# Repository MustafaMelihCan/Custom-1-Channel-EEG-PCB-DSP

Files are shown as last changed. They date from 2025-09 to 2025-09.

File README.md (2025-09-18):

# Custom-1-Channel-EEG (PCB + DSP)

A custom single-channel EEG device developed from PCB design to real-time brainwave visualization.  
Features a low-noise analog front-end with filtering, STM32 DSP (biquads, Welch’s method), and verified alpha detection (~6 dB SNR, ~5× alpha power). See the report to understand how the system works: [Custom 1-Channel EEG Report](docs/Custom_1-Channel_EEG_Device_From_PCB_to_Brainwaves.pdf).

---

## Demo
▶️ Watch the demo video here: [YouTube Link](https://youtu.be/_DtyJymNVPs)  

**Report (PDF):** [Custom 1-Channel EEG Report](docs/Custom_1-Channel_EEG_Device_From_PCB_to_Brainwaves.pdf)

---

## Repository Layout
- `hardware/` – Gerber files, drill files, BOM, LTspice simulations
- `firmware/` – STM32 (CMSIS-DSP) source code and project files
- `docs/` – report, schematics, images

---

## Quick Start
0. To get an overview of the system look at `/docs/1 Channel EEG System Pipeline Final version`. 
1. Build firmware with STM32CubeIDE (or compatible toolchain).  
2. Order PCB using Gerber files from `/hardware/`.  
3. Source components using the BOM in `/hardware/`.  
4. Connect electrodes: **O2** (active), **mastoid** (reference), **Fz/forehead** (DRL).  
5. Stream band powers over USART and visualize with a serial plotter.

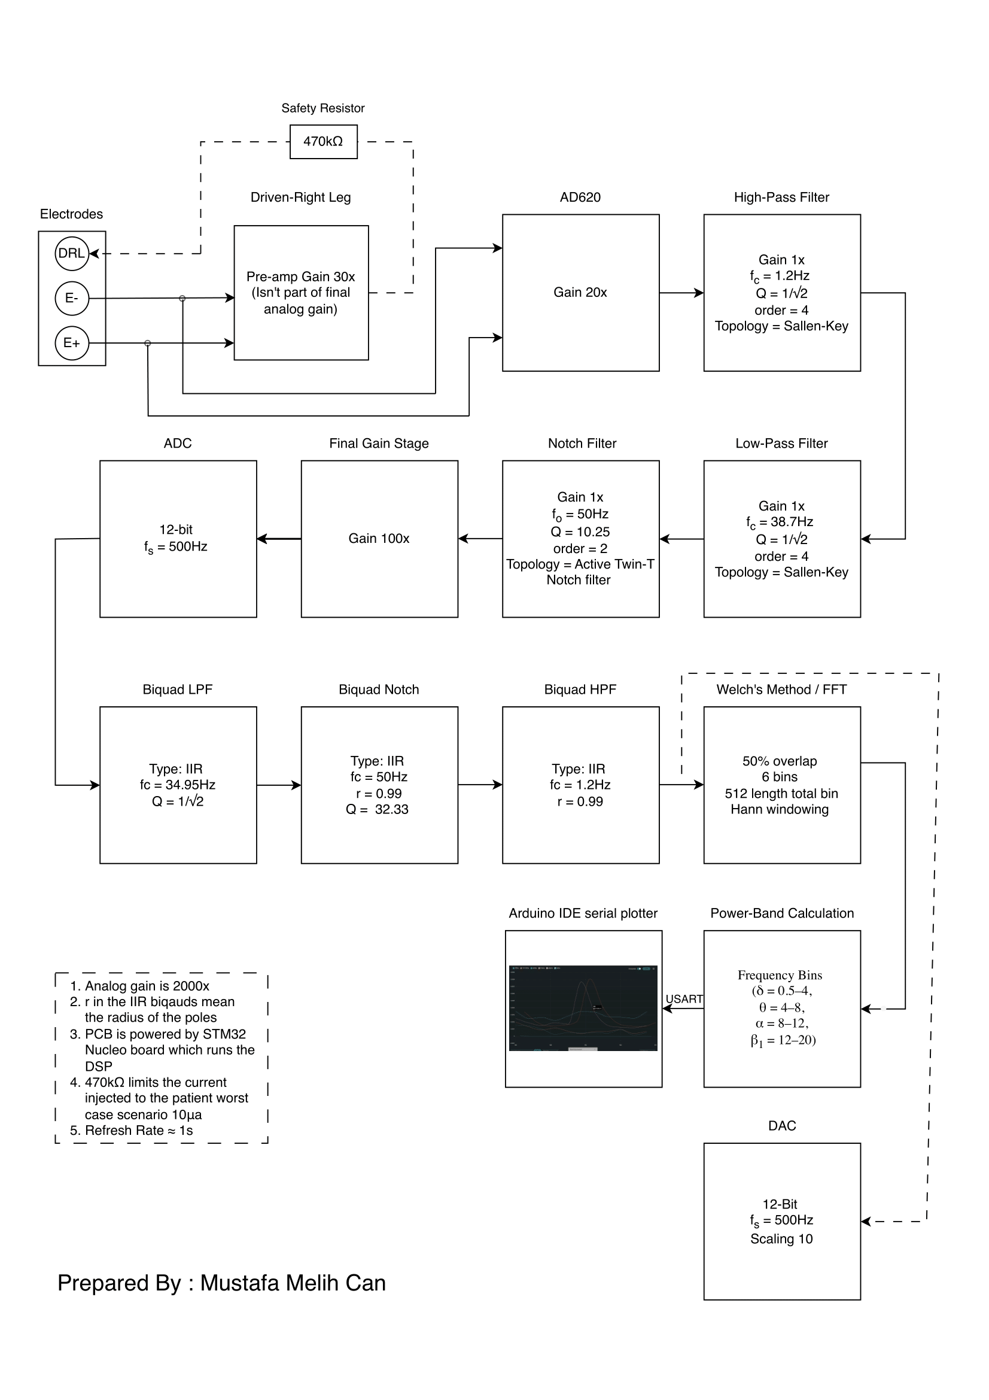
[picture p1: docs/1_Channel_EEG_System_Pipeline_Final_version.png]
EEG System Pipeline


---
## Firmware (STM32 NUCLEO Boards)

The firmware is provided as a zipped STM32CubeIDE project in `/firmware/EEG_Firmware.zip`.  
This code runs on STM32 NUCLEO boards (tested on NUCLEO-F446RE, but portable to other STM32 MCUs).  

### How to use:
1. Download and unzip `EEG_Firmware.zip`.  
2. Open **STM32CubeIDE**.  
3. Go to **File → Import → Existing Projects into Workspace**.  
4. Browse to the unzipped folder and select the project.  
5. Build the project (CubeIDE will compile the code automatically).  
6. Connect your NUCLEO board via USB.  
7. Click the **Run/Debug** button in CubeIDE to flash the firmware.

### Pinout (NUCLEO-F446RE)
- **PC3 (ADC3_IN13)** → EEG analog input from PCB  
- **PA4 (DAC_OUT1)** → Filtered signal output (scope/debug)  
- **PA2 (USART2_TX)** → Serial output to PC (band powers)  
- **PA3 (USART2_RX)** → Not used  
- **PA5 (LD2 LED)** → Status indicator (DMA callbacks)  
- **5V & GND rails** → Power for analog PCB  

Once flashed, the board will:  
- Sample EEG signals from the analog front-end.  The ADC is the PC3 pin. 
- Apply DSP (biquads, Welch’s method) in real time you can see the output on PA4. 
- Stream band power values (Delta, Theta, Alpha, Beta) via USART for visualization.
- You can power the PCB using the 5V and GND rails on the Nucleo Board

**Note:** You can view the streamed data using Arduino IDE’s Serial Plotter or any terminal that supports plotting.  

---
## License
- **Code**: MIT License  
- **Hardware**: CERN OHL-W License (see `/LICENCE_Hardware`)
## Disclaimer
- This project is intended for educational purposes only.  
- The creators accept no responsibility for any harm or misuse resulting from its application.

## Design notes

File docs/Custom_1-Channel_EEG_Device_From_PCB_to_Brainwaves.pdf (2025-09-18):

Mustafa Melih Can | Custom 1-Channel EEG Device: From PCB to Brainwaves

# Mustafa Melih Can Custom 1-Channel EEG Device: From PCB to Brainwaves

# Abstract

This project presents the design and implementation of a custom single-channel electroencephalography (EEG) device developed from printed circuit board (PCB) fabrication to real-time brainwave visualization. The system integrates an analog front-end for amplification, filtering, and common-mode noise rejection with digital signal processing on an STM32 microcontroller. Core algorithms include biquad filters and Welch’s method for spectral estimation, enabling reliable suppression of 50 Hz interference and white noise. The device was validated through the detection of alpha activity during eye closure, achieving a signal-to-noise ratio of approximately 6 dB and an alpha power increase of 5.2 times compared to the eyes-open condition. Despite limitations of its single-channel architecture and sensitivity to electrode placement, the results demonstrate that a low-cost DIY EEG can capture meaningful neural activity. The project provides a foundation for future improvements such as multi-channel expansion, wireless communication, and advanced artifact rejection techniques. It allows for a Digital Signal Processing (DSP) based EEG device that can be used in research / commercial / DIY use.

# Introduction

Electroencephalography (EEG) is a non-invasive method of measuring brain activity by detecting voltage fluctuations generated by neural oscillations. It plays a crucial role in clinical diagnostics, neuroscience research, brain–computer interface (BCI) applications, and consumer neurofeedback devices. However, most commercial EEG systems are costly, complex, and designed for multi-channel use, making them less accessible for students, researchers, and hobbyists who seek to explore neural signals at a smaller scale. At the same time, do-it-yourself (DIY) EEG projects often struggle with fundamental challenges such as low signal amplitude, environmental noise, and electrode stability. To address these limitations, this project set out to design and implement a custom single-channel EEG device that is affordable yet capable of reliably detecting meaningful brainwave activity. The system integrates an analog front-end with amplification and filtering, digital signal processing on a microcontroller, and real-time visualization of EEG band powers. By focusing on detecting alpha activity during eye closure as a proof of concept, the project demonstrates how a streamlined design can bridge the gap between academic prototyping and practical EEG experimentation. The project aims to create a reliable system to detect brain signals.

# System Overview

The EEG consists of three main parts in this project. The system is divided into three stages: Analog, Digital, Display. Because the main purpose of this study is to make a single Channel device and mixed signal analysis Analog and Digital parts of the project got more attention. The Analog side design flow progressed as LTspice simulation, Breadboard Filter Prototyping and testing, to PCB design, soldering and testing. You can see the full project pipeline on Figure 1.

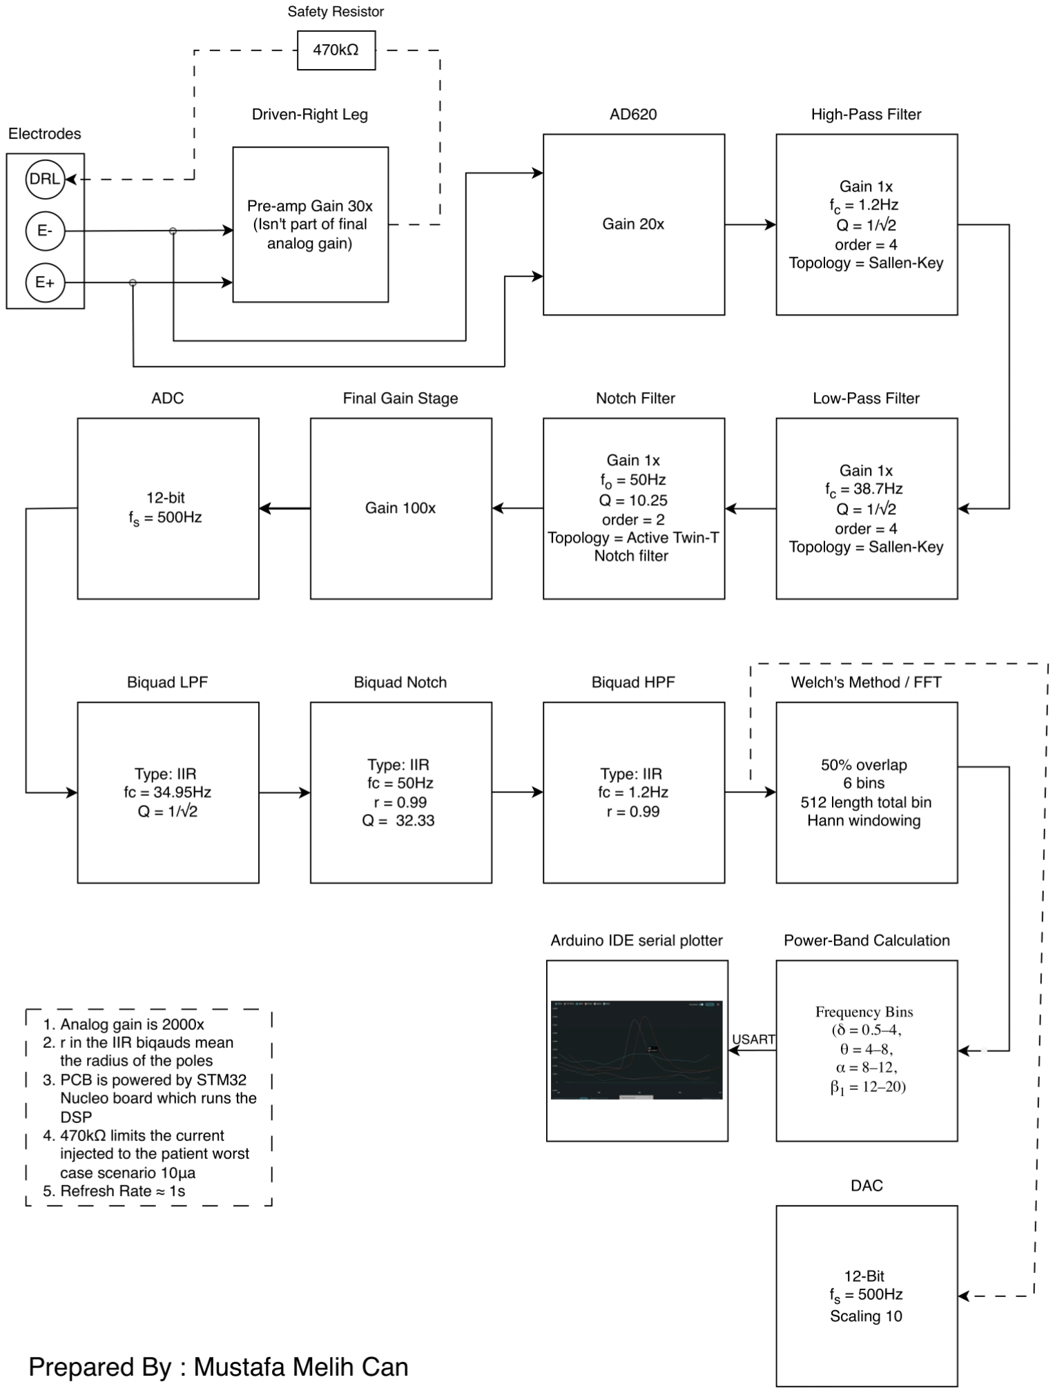
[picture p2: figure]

Figure 1. 1 Channel EEG System Pipeline

The analog stages “prepares the signal” by adding a total gain of 2000x and does filtering for a clearer and aliasing-free signal. According to Nyquist theorem fs > 2fmax; I chose fs = 500Hz (~10× fmax) to make the signals smoother on the DAC.

# Hardware Design

Ok the hardware has two important roles. The first is Common Mode Noise Rejection (CMNR) that is accomplished through Driven Right Leg (DRL) and Instrumentation amplifier (INST AMP) stages. The second role is filtration and adding gain.

## Common Mode Noise Rejection

The DRL is the first line of defence in us improving Signal to Noise Ratio (SNR). It basically averages the E+ and E-, adds gain, inverts it and sends it back to the body with a current limiting resistor. We basically use an adder topology since 30 ⁽x1+x2

)
2

= 15(x1 + x2

).

Here is the DRL block and the INST AMP schematic on figure 2:

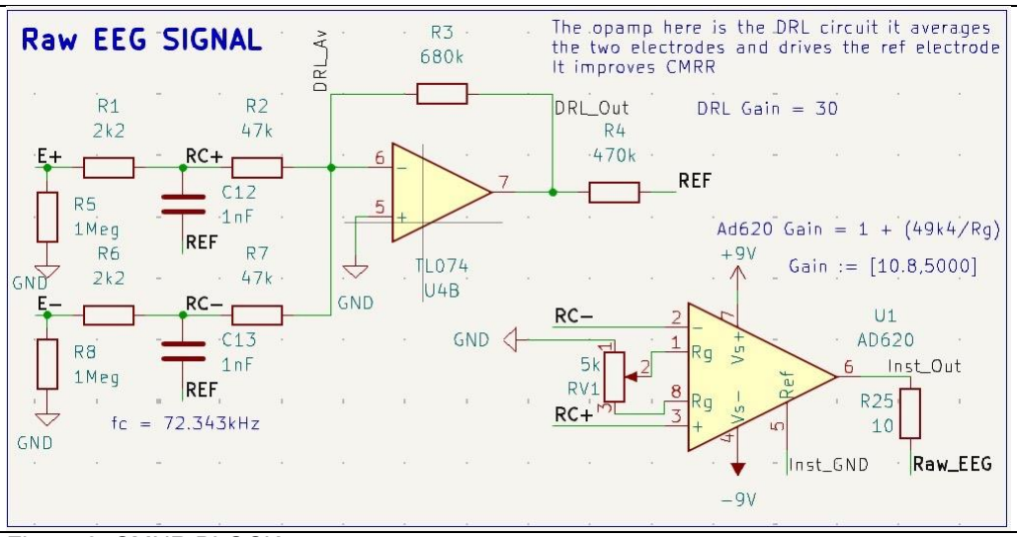
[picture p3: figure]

Figure 2. CMNR BLOCK

As you can see the basic DRL has some additions in design. I added a 1MΩ to the GND to make sure that the electrodes wouldn’t float if they are not connected to anything else. Then the electrode stages depicted by E- and E+ connects to an RC lowpass stage with a fc at 72.34 kHz this is done to clean the signal before the signal reaches the INST AMP. And since the fc is far away we don’t need to make it active and can get away with a passive one. Then we have the DRL stage with the H(s) as follows:

30 ⋅

Vin1

(s) + Vin2

(s)
2

= Vout(s)

Plus the DRL has a current limiting which limits the max current to: Vmax
R4 =

5V
470kΩ

= 10μA

After the DRL stages we feed the RC+ and RC- stages to our INST AMP with a gain setting equation as follows:

Gain = 1 +

49k4
RV1

: {RV1 ≔ [1,5k]}

RV1 is a potentiometer (POT) so we can write the gain range of the INST AMP as follows: Gain : {[10.8,5000]}
However, the gain i used is 20x for the inst amplifier and for your project it should get max of 100 to 200 to not swamp the EEG signal with further 50Hz hum and white noise we can add the further gain needed later. Why did we choose the gain 20x for now because alpha jumps and general eeg signals are around 10 to 20uV we if we want to make them as large as possible however we generally have a 50Hz hum that can be as large as 100mV to 250mV.

Considering these the max gain is calculated to maximise eeg signal while not saturating our opamp range ±5V ; when we pick the gain around 20x that is the ideal spot hum and eeg signal volts are as follows:
VEEG ⋅ G = 20μV ⋅ 20 = 0.1mV V50Hz ⋅ G = 250mV ⋅ 20 = 5V As you can see the main constraint for our initial INST AMP gain stage is the environmental hum. The gain setting is set using a POT as you can see from the Figure 2. Pot works as a INT AMP gain setting.

## Filtering and Gain Stage

### a. High-Pass Filter (HPF)

The purpose is to remove motion, breathing, DC offset and heartbeat artifacts below 1.2Hz. 4th degree filter is decided to be made because the phase distortion by the 4th order is considered acceptable, therefore the order is not a constraint. And breathing artefacts and heartbeat artefacts wanted to be removed as efficiently as possible. So by cascading two second order HPF’s i decided to get a 4th order HPF the second order HPF transfer function is as follows:

HHP(s) =

s

2

s

2 +

ωc
Q

s + ωc

2

The Sallen-Key 2nd order HPF topology is used. Please see the appendix to see the derivation of the transfer function which results in our topology seen in figure 3. and the transfer function seen is as follows:

HHP(s) =

s

2

s

2 +

c1 + c2
c1 ⋅ c2 ⋅ R2

s +

1
c1 ⋅ c2 ⋅ R1 ⋅ R2
Please check appendix for the derivation.

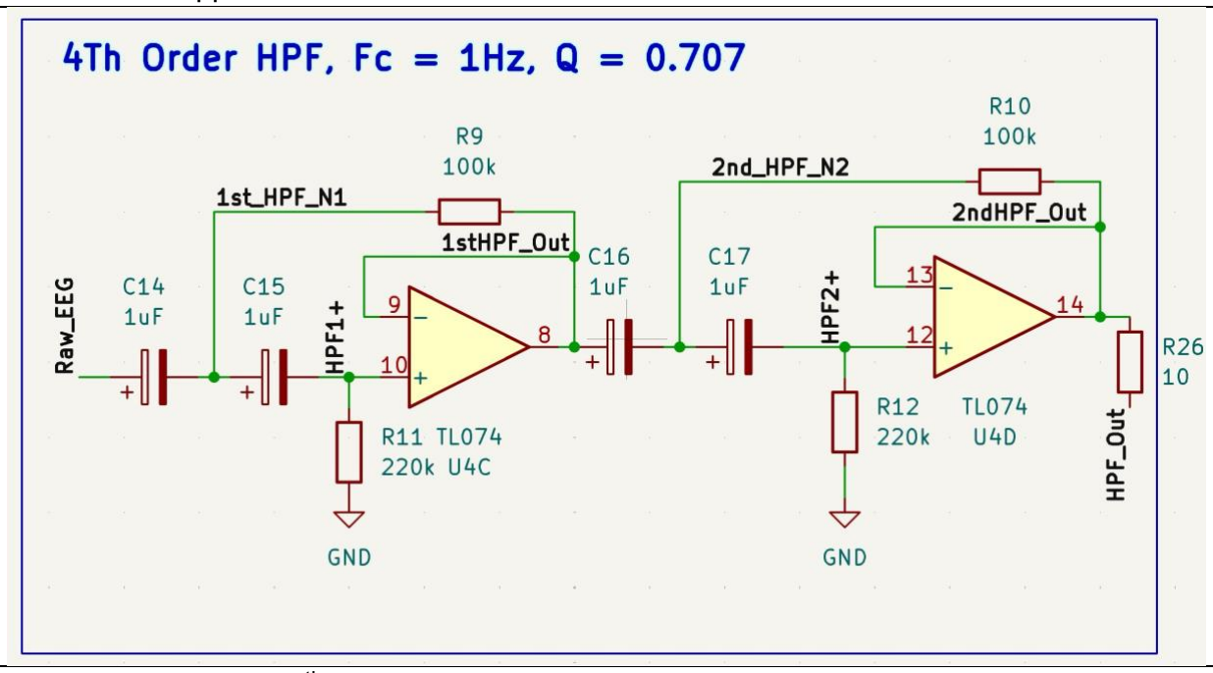
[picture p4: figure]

Figure 3. Sallen-Key 4

th order HPF

Using the transfer previous transfer functions we get the equalities:

ωs
Q

=

c1 + c2
c1 ⋅ c2 ⋅ R2

ωs

2 =

1
c1 ⋅ c2 ⋅ R1 ⋅ R2
Our desired fc = 1Hz and Q =

1
√2

which creates a Butterworth filter. fc is chosen as higher than

usual eeg devices to remove the breathing and heartrate artefacts more efficiently since we cannot use ICA algorithm like multiple channel electrodes we need to remember that we have a single channel eeg so cleaner is always better and our purpose is to catch alpha and low beta waves so we can compromise some data lose in the delta wave range. We can choose the capacitor values arbitrarily and values that are physically easy to find and implement we can choose both capacitors as 1μF which when we seperate R1 and R2 we get the following equations (R1=R11=R12, R2=R9=R10, C1=C2=C14=C15=C16=C17):

R2 =

Q ⋅ (c1 + c2

)
c1 ⋅ c2 ⋅ 2 ⋅ π ⋅ fc

= 225kΩ ≈ 220kΩ

R1 =

1
c1 ⋅ c2 ⋅ (2 ⋅ π ⋅ fc

)

2 ⋅ R2

= 112kΩ ≈ 100kΩ

To verify we plug our R1, R2, C1, and C2 back to our equations to find fs and Q. Which when we plug them in we get them as:
Q = 0.741, fc = 1.08Hz

### b. Low-Pass Filter (LPF)

The purpose is to remove EMG and power line noise and also to act as our antialising filter HPF for further DSP application. A similar decision made to HPF made in our LPF as well a 4th order filter with –24dB/octave is chosen. Because both EMG which is between 30Hz to 100Hz range and 50Hz hum is are strong noise sources which we want to eliminate as strongly as possible. The topology is at Figure 4.

Figure 4. Sallen-Key 4th order LPF
A similar design process to HPF is followed therefore the details are omitted. However the final Q and fs are as follows:
Q = 0.755, fs = 38.79Hz

### c. Notch Filter

The purpose is to remove power line noise in Turkey with standard 50Hz. An active Twin-T notch filter is used for our design. Because we can set the Q using a simple voltage divider and the Twin-T topology doesn’t determine the Q and we can use them to control the center frequency also with this topology we only use 2 opamps. The topology can be seen in Figure 5.

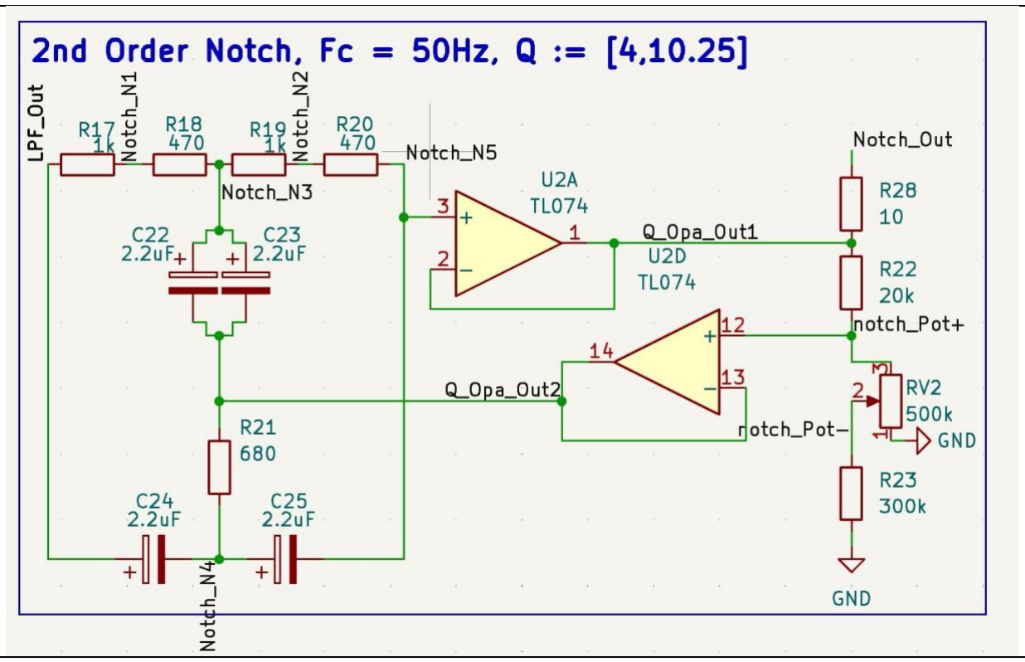
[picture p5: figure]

Figure 5. Active Twin-T Notch Filter
For context of my circuit lets the set values are as follows: R17 + R18 = R19 + R20 = R, R21 =
R
2

, C22 = C23 = C24 = C25 = C
The following contains the transfer function of the Notch Filter:

HN(s) =

s

2 + ω0

2

s

2 + s

ω0
Q

+ ω0

2

=

s

2 + (

1
RC)

2

s

2 + s

4 ⋅ (1 − K)
RC + (

1
RC)

Where:

K =

RV2 + R23
R22 + RV2 + R23

Q =

1
4(1 − K)

so, Qmin = 4, QMax = 10.25

Since RV2 is a potentiometer, it was used to tune the effective gain range [4,10.25], so that it can attenuate 50Hz while not cause ringing in the circuit that is why it is capped at 10.25 value.
f0 =

1
2πRC

= 50Hz

f0 =

1
2πRC =

1
2π ⋅ 1.470 ⋅ 10³ ⋅ 2.2 ⋅ 10⁻⁶ = 49.21Hz ≈ 50Hz

Be careful when increasing the Q on your project with the potentiometer because as you can see the center frequency in our case is around 49.21Hz and if we increase the Q very high such as 30 40 we might make the notch very steep and deep causing our filter to miss the center frequency which is 50Hz in our case.

When we simulate all of the filters in LTspice we get the following filter response:

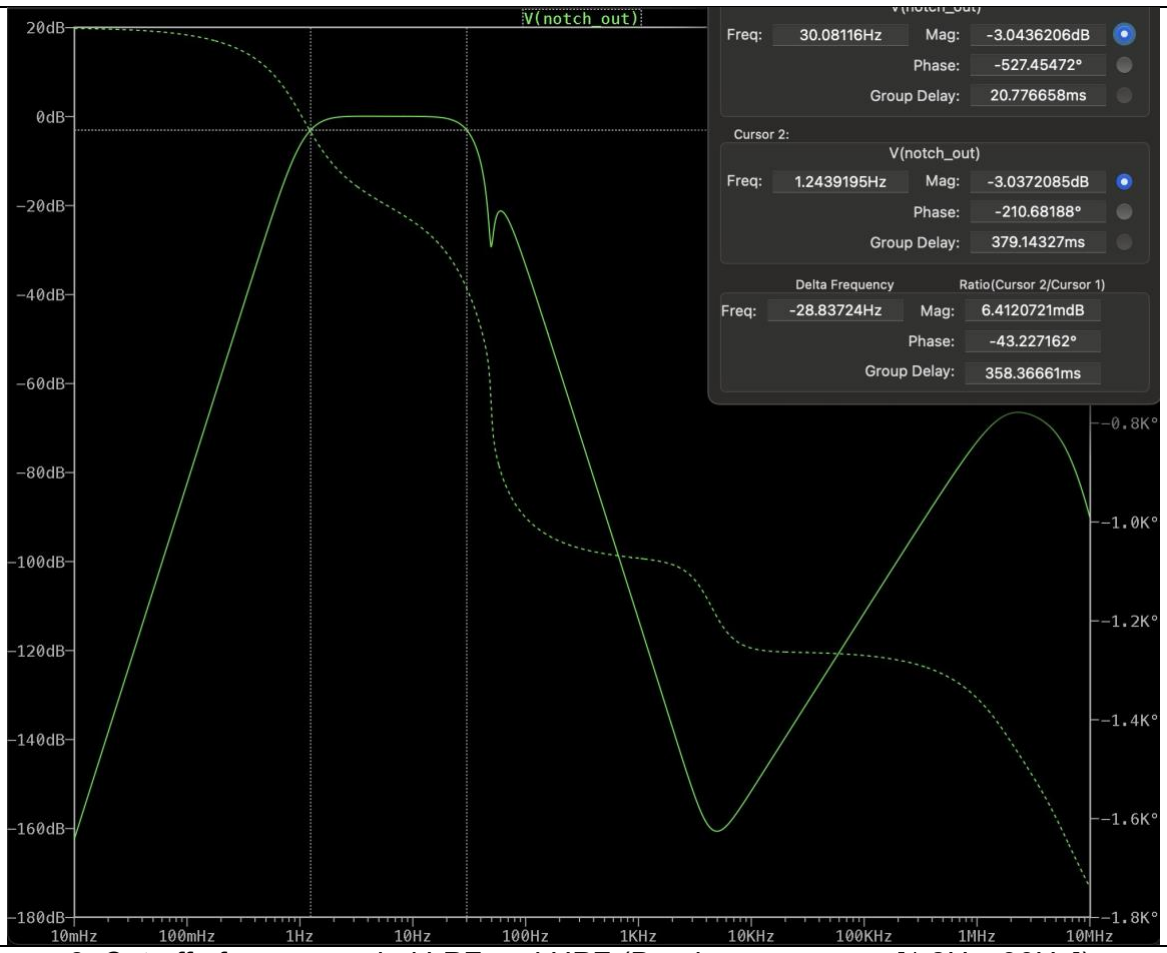
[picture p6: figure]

Figure 6. Cut off of our cascaded LPF and HPF (Bandpass range := [1.2Hz, 30Hz])

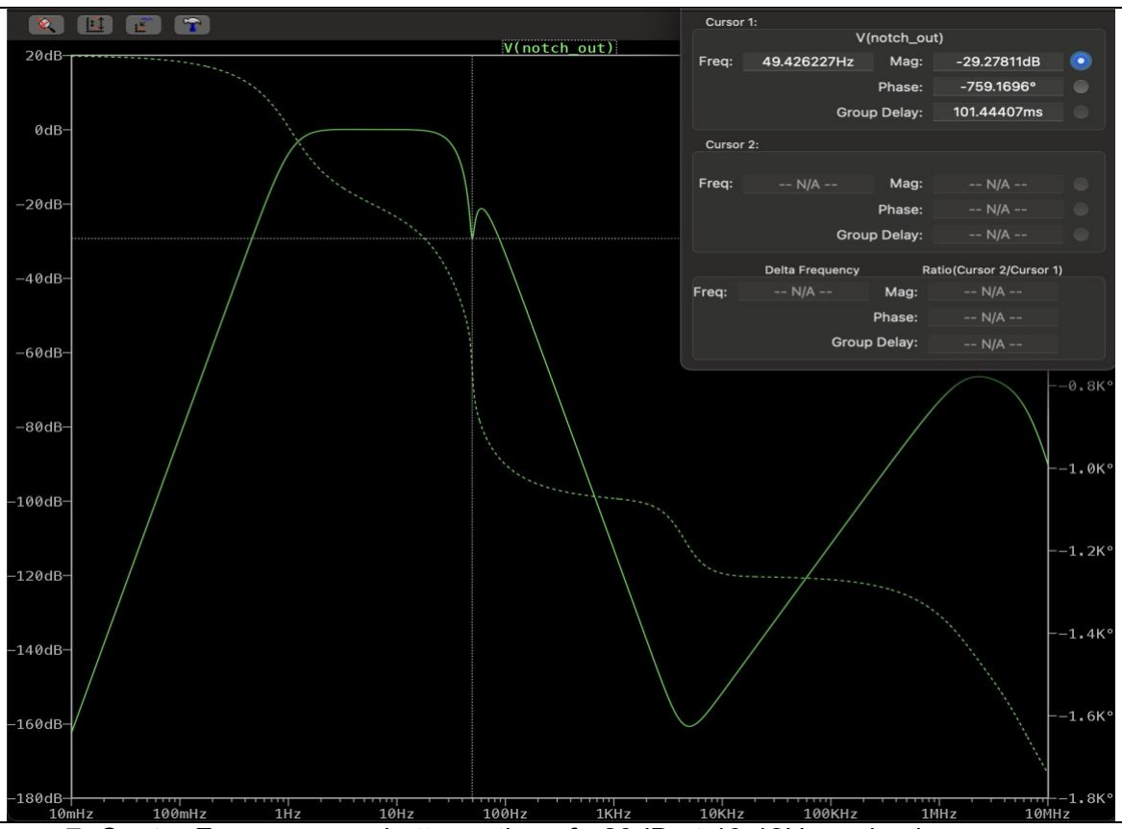
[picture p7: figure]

Figure 7. Center Frequency and attenuation of –29dB at 49.42Hz mains hum

### ç. Final Gain Stage

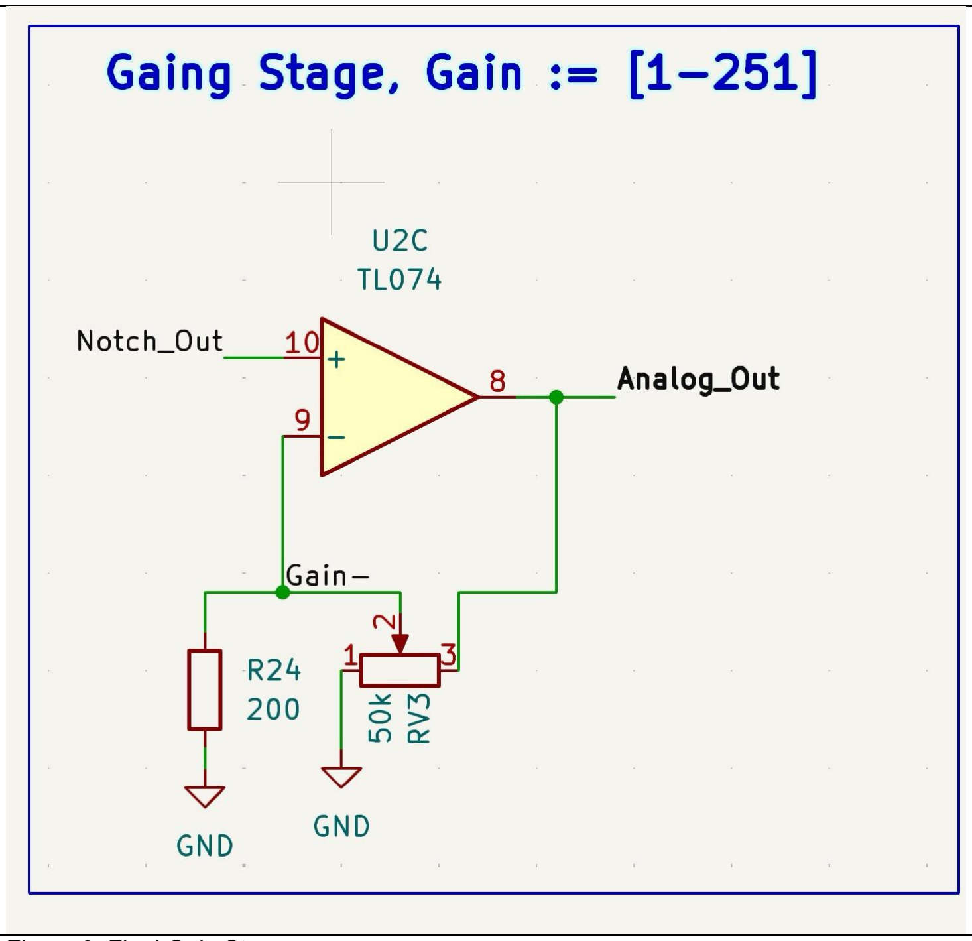
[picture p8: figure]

Figure 8. Final Gain Stage The Gain function is as follows:

Gain = 1 +

Rv3
R2

, Rv3 ∈ [0,50kΩ], R2 = 200Ω

This final stage gives a gain setting with a potentiometer between 1x to 250x. Allowing me to set the output of the PCB between the ADC optimum range which is between 0V and 3.3V. This gain stage allows for a DC offset adder as well because the PCB output is generally is around 200mV so we can easily increase the gain to add a 1.65V DC offset that will make the output of the PCB optimum for the ADC stage. If yours doesn’t come out like that you can add a DCshifter which you can find the design on the appendix section.

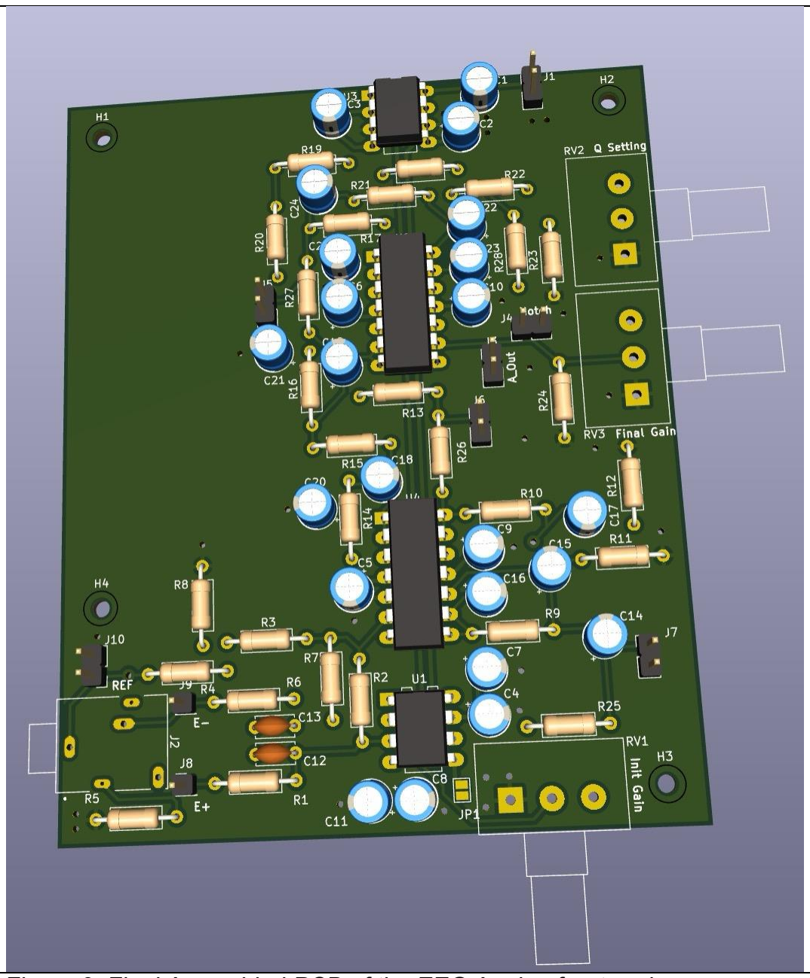
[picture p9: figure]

Figure 9. Final Assembled PCB of the EEG Analog front-end

# Software Design

The software in this project completes the rest of the functionalities of the EEG. There are two functions that the digital side accomplish:
1) Digital Signal Processing
a. Welch’s method (Reducing white noise)
b. ARMA Biquad Filters (Remove hum, artefacts)
2) Displaying EEG Frequency Bands
a. Do Fast Fourier Transform (FFT) and calculate Power Spectral Densiy (PSD) to show different frequency ranges (Alpha, Beta, etc.)
b. Data Display: Using USART to show data on a serial display
An appropriate Sampling frequency 500Hz is chosen. It is 15x the max frequency (35Hz) that our system will be interested. And is well over the nyquist theorems minimum sampling frequency (fs>2fmax).

## Digital Signal Processing

### A. Biquad Filters

A biquad filter basically means a two zero, two pole cascading second order (SOS) filters. The SOSs can be cascaded without making the whole system unstable they act as the building blocks of our larger complicated filtering systems. In this instance we want to create the same filters we created in the analog side to further clean our signal digitally. A biquad equation has the form:

H(z) =

b0 + b1z

−1 + b2z

−2
a0 + a1z

−1 + a2z

−2
The form then can be turned into the difference equation using inverse Z transform:

y[n] = b0x[n] + b1x[n − 1] + b2x[n − 2] − a1y[n − 1] − a2y[n − 2].

The difference equaion results in the following figure configuration:

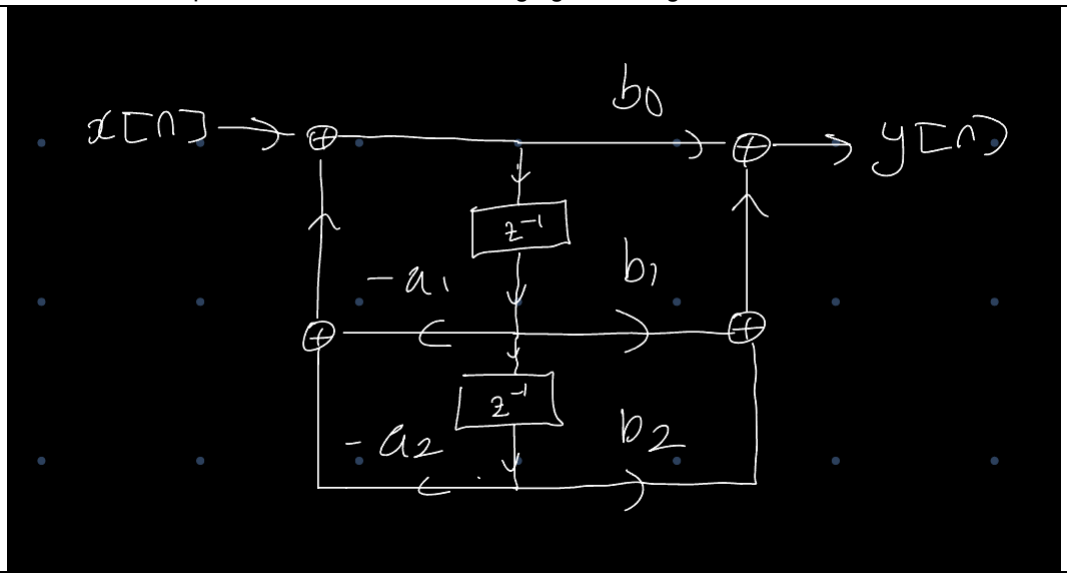
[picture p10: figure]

Figure 10. Cascade form of ARMA Biquad Filter Block Diagram

By using CMSIS-DSP library of the ARM cortex MCU’s when we get the coefficents of our filters we basically can plug them in the CMSIS functions. Which will do the multiplying and shifting of our buffer for us which depicted on the Figure 10.

### A1. Biquad Notch Filter

To get a notch filter we are going to put zeros at 50Hz and poles around 50Hz with the radius r1. Using our sampling frequency, to calculate that region we use the formula:
ω = ΩT;
Where Ω means the analog angular frequency, ω is the digital angular frequency and, T is our sampling period.

Assuming we want to place our zeros and poles at 50Hz then to find where are we going to place them between [-π, π] which is digital angular frequency range:

ω0 = Ω0T = 2π ⋅

f0
fs

= 2π ⋅

50
500 =

π
5
Here we see that our poles/zeros should be on the π/5. However, since our filter needs real coefficients we are going to put them at ω0 =

π
5

, −

π
5

on the complex plane. Plus we going to place the zeros right on the unit circle making a very deep notch and placing the pole near the zero but not at unit circle. This is done to dampen the notch effect and control the notch by controlling the radius of our poles. Lets see the mathatical formulation:

HN(z) =

(1 − z
−1e

j

π
5) (1 − z
−1e

−j

π
5)

(1 − z
−1r1e

j

π
5) (1 − z
−1r1e

−j

π
5)

HN(z) =

1 − 2 cos (

π
5

) z
−1 + z

−2

1 − 2r1 cos (

π
5

) z
−1 + r1

2
z

−2

Therefore our notch equation is completed.

Figure 11. Notch Filter Response |H(e^jw)|

When we try some r1 values and simulate the results on Matlab we get an r1 value of 0.99. Which we can see the results on Figure 11. and the pole-zero plot on figure 12.

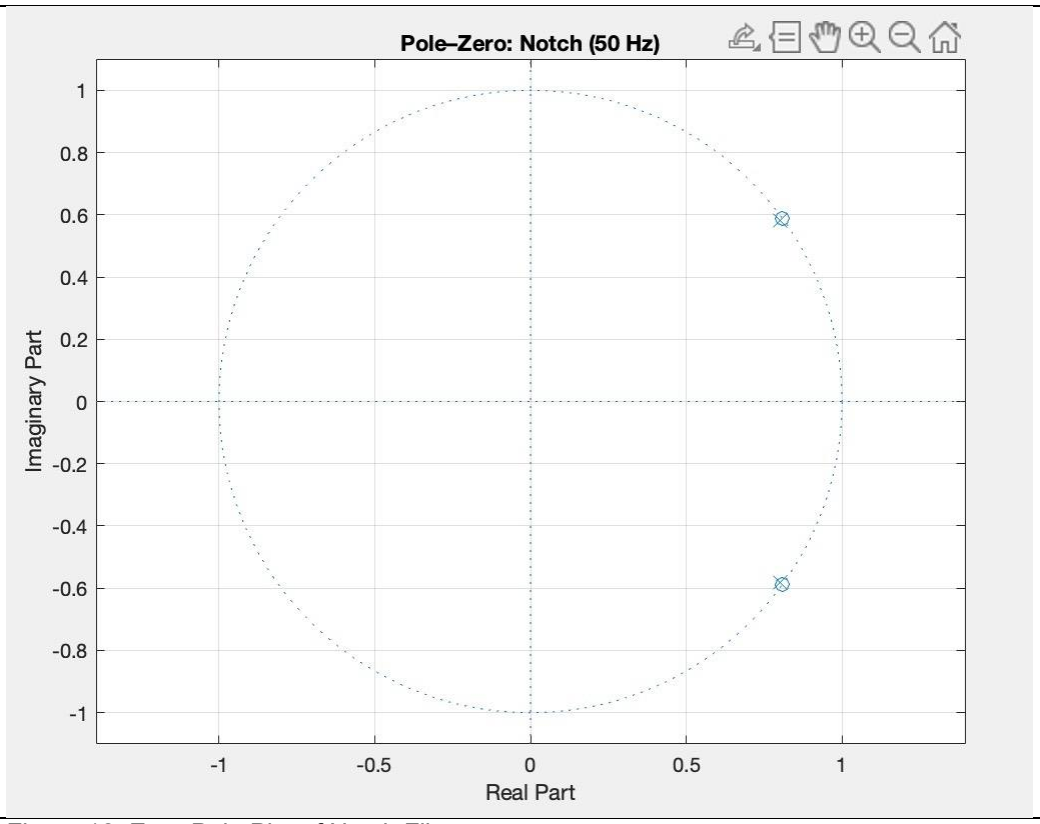
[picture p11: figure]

Figure 12. Zero-Pole Plot of Notch Filter

The final coefficients are:
bnotcℎ = [1, − 2 ⋅ r1 cos (

π
5

) , 1]

anotcℎ = [1, −2r1 cos (

π
5

) , r1
2

]

### A2. Biquad HPF

Standard HPF and LPF biquad designs are used. The HPF is designed as:

HHP(z) =

(1 − z

−1
)

2
(1 − r2z

−1)

2

HHP(z) =

1 − 2z

−1 + z

−2
1 − 2r2z

−1 + r2

2
z

−2
And:
r2 = exp (−

2πfHP
fs

) = exp (−

2π1.2
500 ) = 0.985

Here is the Pole-Zero plot of the filter:

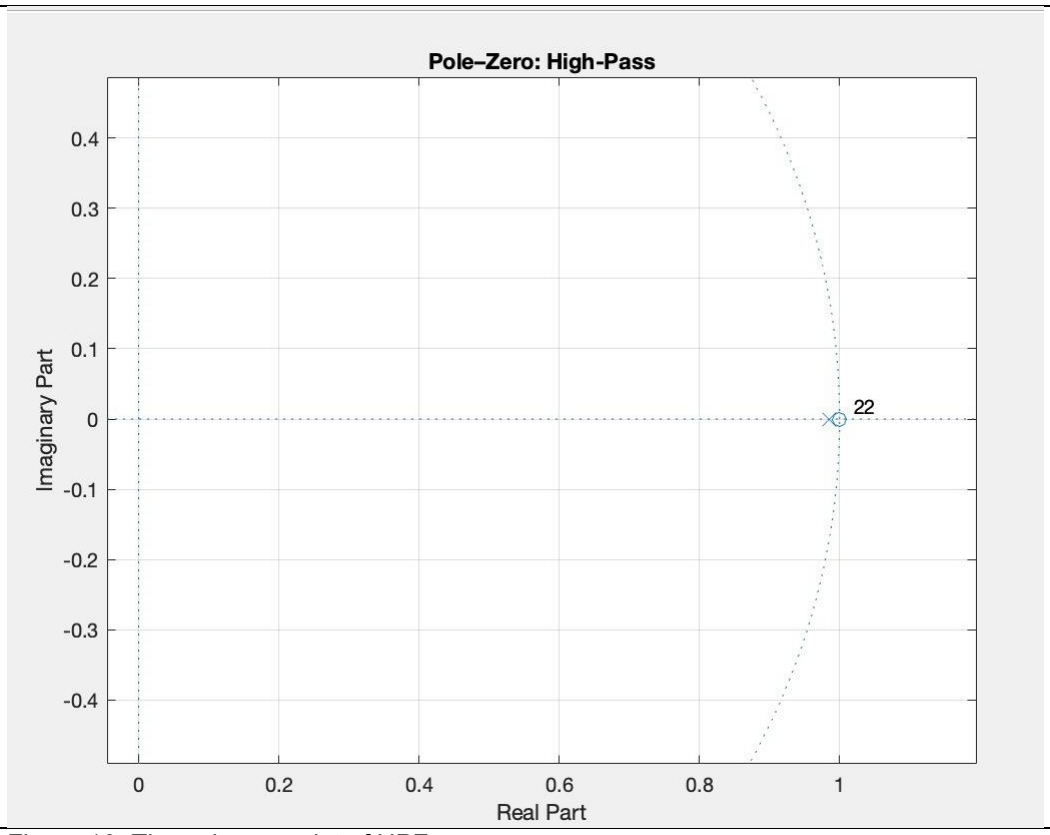
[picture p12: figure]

Figure 13. The pole-zero plot of HPF
As you can see from the figure 13. our biquad pole and zeros are on the real axis which is consistent with our desgin choices and our application. Now we must find the HPF coefficients therefore the coefficients for the HPF is found:
bHPF = [1, − 2, 1];
aHPF = [1, − 1.980, 0.9801]; With these coefficients we get the following filter response:

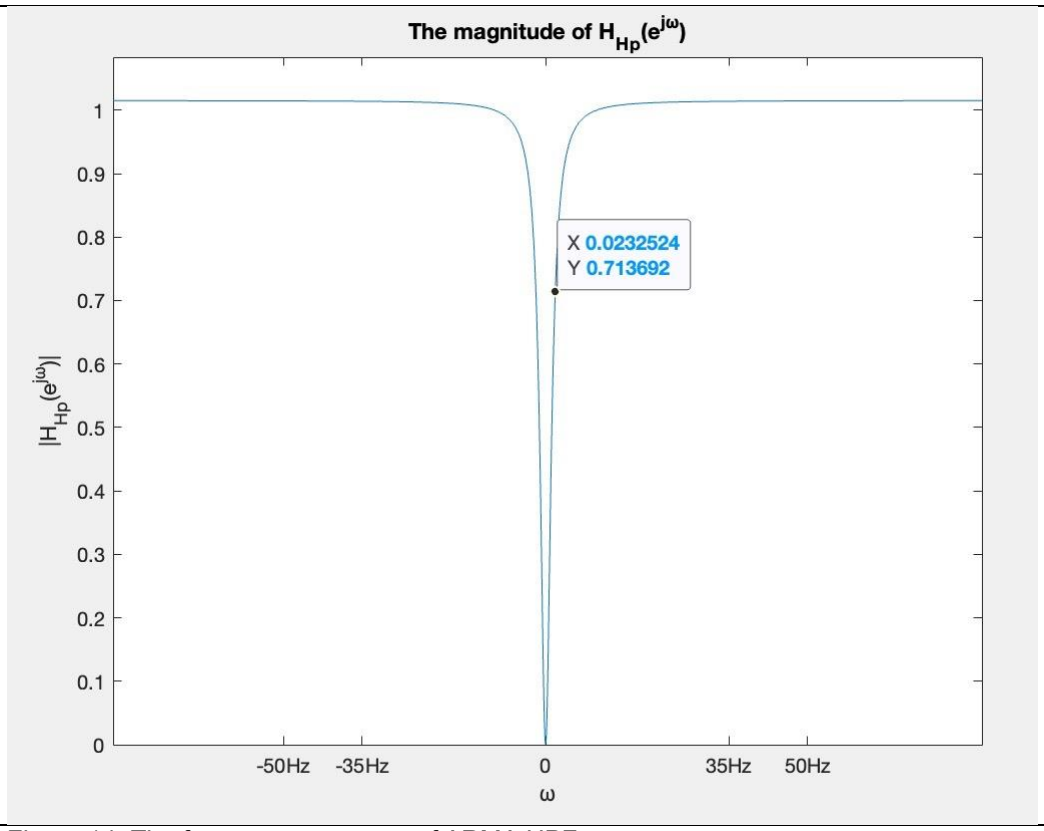
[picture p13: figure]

Figure 14. The frequency response of ARMA HPF

### A3. Biquad LPF

A bilinear approach is used to LPF design. Here is the analog 2nd-order butterworth LPF:

HHP(s) =

Ωc

2

s

2+

Ωc
Q

s+Ωc

2

, Q =

1
√2

,Ωc = 2πfc

When we do the bilinear mapping we get:

Ωc =

2
T

tan (

ωc
2

) , s =

2
T

⋅

1 − z

−1
1 + z

−1

, T =

1
fs

, ωc =

2πfc
fs
Then we expand to get the final z equation as:

HLPF(z) =

0.0366 + 0.0731z

−1 + 0.0366z

−2
1 + − 1.3909z

−1 + 0.5372z

−2
Using these coefficients when we plot the pole-zero diagram we get:

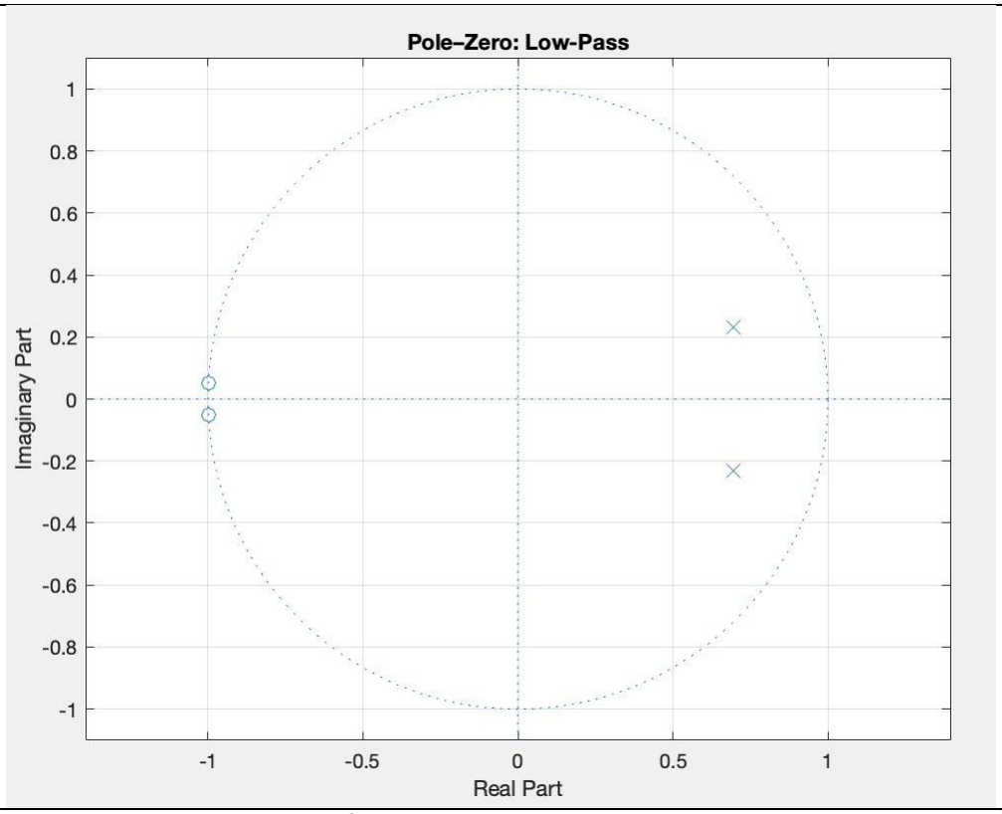
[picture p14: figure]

Figure 15. The pole-zero plot of LPF
As you can see from Figure 15. that our poles are on the unit circle at the Nyquist frequency and our zeros have a phase of 0.32 radians and radius of 0.733 which means it is on the 25.46 Hz frequency in the Ω (analog angular frequency) domain. This is consistent with our Bilinear transform design.
Therefore our coefficients are:
bLPF = [0.0366, 0.0731, 0.0366]; aLPF = [1, −1.3909,0.5372]; Here is the frequency response of our LPF becomes:

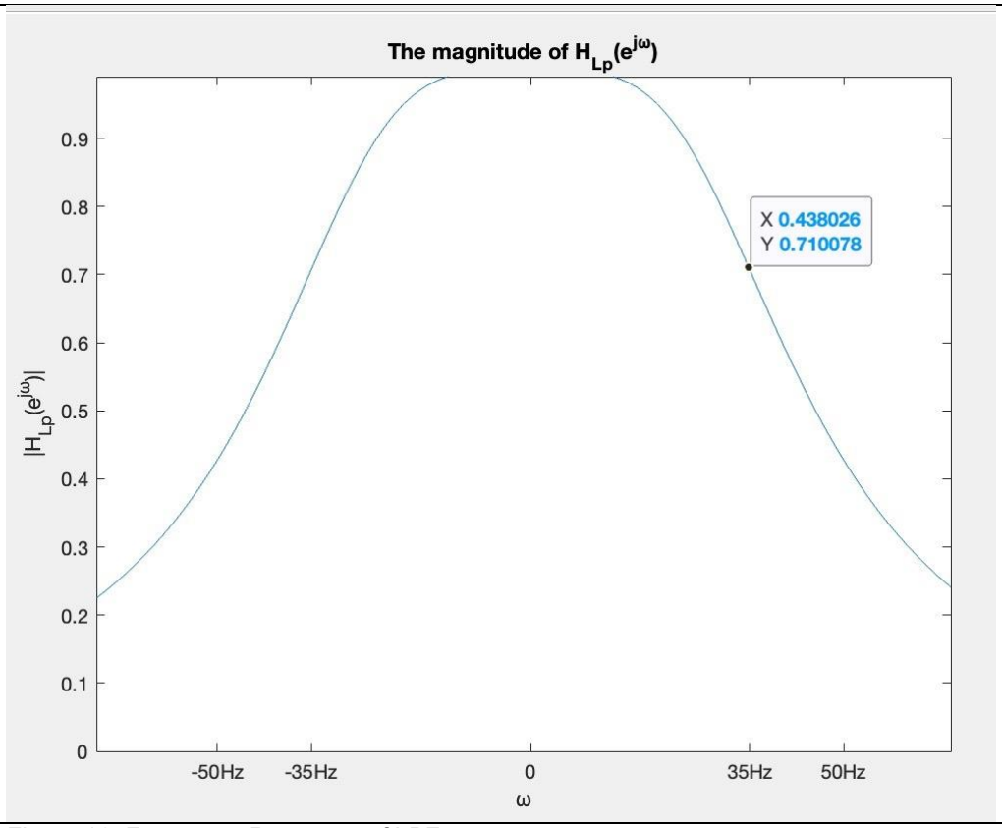
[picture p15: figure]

Figure 16. Frequency Response of LPF

You can check the github for the full code implementation of these filters. Also here are the final plots for the all three cascaded ARMA filters:

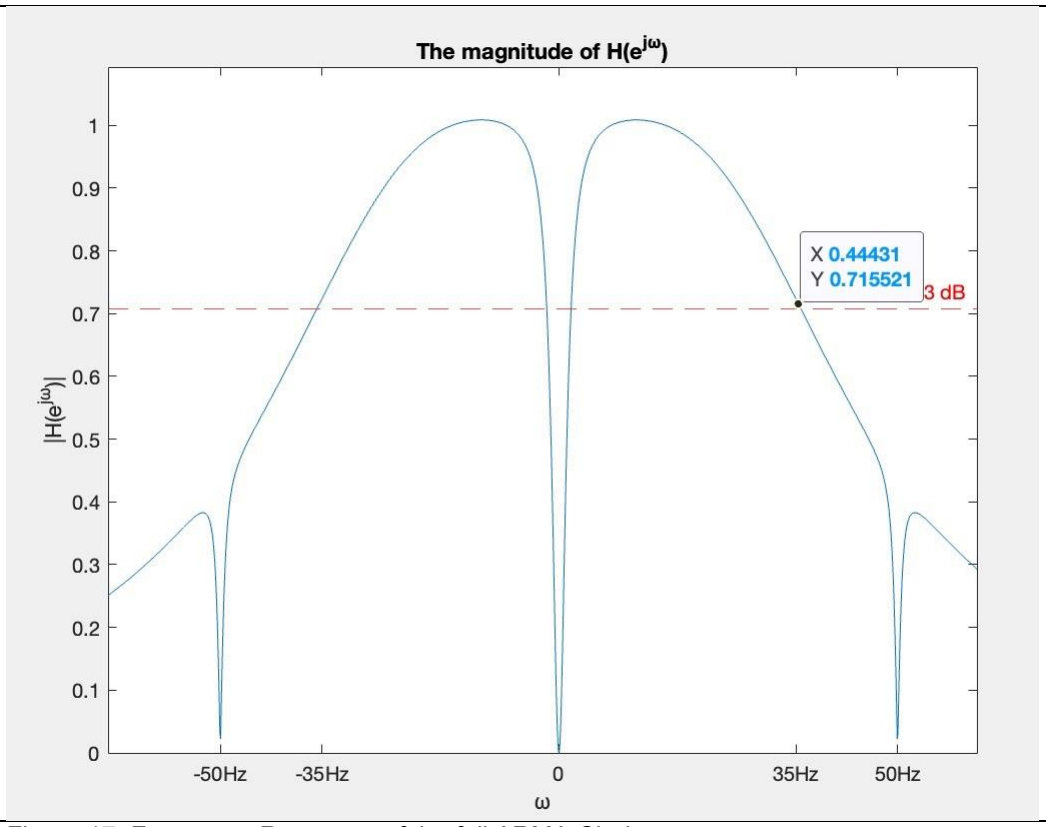
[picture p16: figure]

Figure 17. Frequency Response of the full ARMA Chain

Figure 18. Pole-zero plot of the full ARMA Chain

### B. Welch's Method

The Welch’s method basically prepares the data for a FFT application the purpose of it is to remove white noise probabilistically. It basically takes the average of FFT windows allowing for us to probabilisticly construct the time correlated data such as alpha jumps when a blink occurs and destruct the time unccorralted such as white noise. So in order to make this happen we are going to choose a bin size which in our application is best set at 512 which will approoximately give 1Hz bins which is enough resolution to calculate Power Spectral Density (PSD) across different bands.

fs
Bin size =

500
512 = 0.976Hz resolution

The algorithm is basically is 6 steps:
1. ontinuously shift incoming samples into a 512-sample buffer
2. From this buffer, take the first 256-sample segment (with 50% overlap) as the analysis window
3. Apply hemming window to the segment
4. Compute a 256-point FFT to obtain the frequency spectrum
5. If this the third 256-point FFT (i.e., covering the full 512-sample buffer), shift to the next buffer and repeat.
6. Average with all 6 FFT blocks therefore reducing variance (basically white noise)

You can check github for the full implementation of FFT/Welch’s algorithm.

## Displaying EEG Frequency Bands

### A. FFT and PSD

As we have our cleaned data we are going to take the FFT of our signal. After filtering, the EEG signal is transformed into the frequency domain using the Fast Fourier Transform (FFT). The FFT efficiently computes the Discrete Fourier Transform (DFT):

X[k] = ∑ x[n]e
−j⋅

2π
N

kn

N−1

n=0

, k = 0,1, … N − 1

In Practice the algorithm goes like this:
- The EEG stream is divided into 256-sample segments.
- Each segment is windowed (Hamming) to reduce spectral leakage.
- A 256-point FFT is computed using the CMSIS-DSP library on the STM32 microcontroller.
- The squared magnitude of the FFT gives the power spectrum of that segment.
- By averaging multiple overlapping spectra (Welch’s method), the Power Spectral Density (PSD) is obtained.
- The PSD is then integrated over standard EEG frequency bands (delta, theta, alpha, beta) to calculate EEG band powers. Which basically means adding the subsiquent indeces of our FFT output buffer and squaring it.

### B. Data Display

Once the EEG signal is filtered and transformed into the frequency domain, the final task is to make the results observable in real time. In this project, the STM32 sends the calculated band powers (Delta, Theta, Alpha, Beta) to a PC via USART serial communication. The arduino IDE serial plotter receives this powers and plots them continuously every second, allowing visual tracking of band activity. This setup makes it easy to observe alpha jumps when the subject closes their eyes, while still providing the option to stream raw time-domain signals for debugging. This is done by using DAC at the same sampling frequency and writing our filtered data on the display out of the board therefore we can show it on our oscilloscope. You can see that on Figure 19. The blue line is the DAC output and yellow is the input to our DSP system. The approach is modular and can be extended to more channels or alternative visualizations (e.g., bar graphs, scrolling waveforms, or spectrograms).

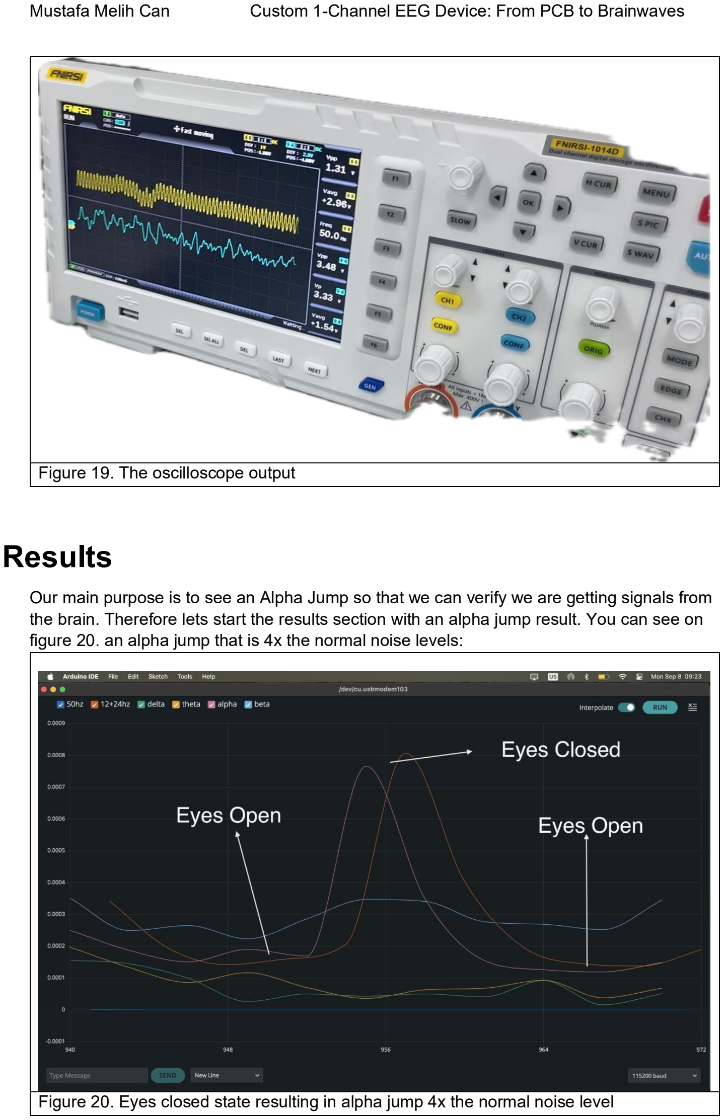
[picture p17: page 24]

Figure 19. The oscilloscope output

# Results

Our main purpose is to see an Alpha Jump so that we can verify we are getting signals from the brain. Therefore lets start the results section with an alpha jump result. You can see on figure 20. an alpha jump that is 4x the normal noise levels:

Figure 20. Eyes closed state resulting in alpha jump 4x the normal noise level

The figure 20. shows an Occular test done on O2 site on the brain of the patient. It is expected to see an alpha jump when the patient closes their eyes resulting in a jump in the alpha PSD. As you can see the resulting jump is 4x which is very significant. (see the end of the results section to see SNR and ALPHA ratios)

Further real time results for the system can be seen on the video: https://youtu.be/_DtyJymNVPs

Once soldered and tested the final PCB was assembled Figure 21. shows the completed analog front-end board.

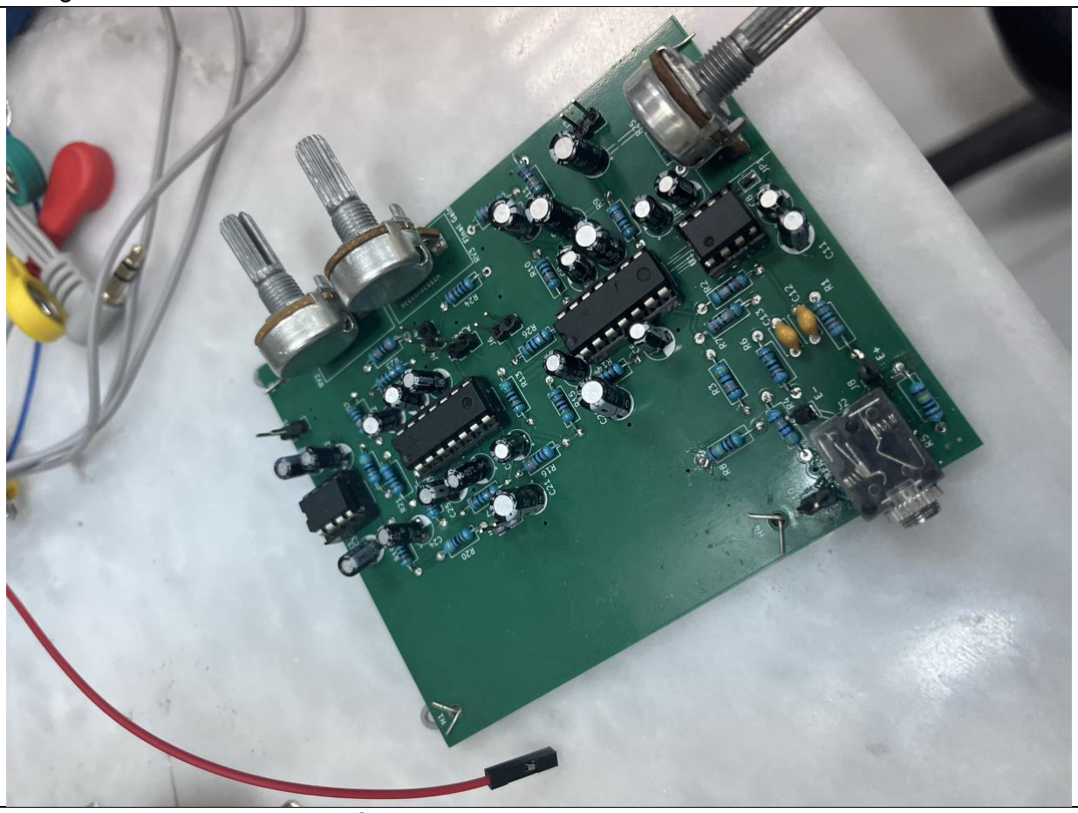
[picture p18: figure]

Figure 21. Fully assembled PCB

To improve SNR, the electrodes were shielded and twisted to minimize external interference. The electrodes shielding has a ground connection that also is connected to the PCB as well.
The | Brown | wire | shown | in | Figure | 23. | works | as | our | shielding | ground.

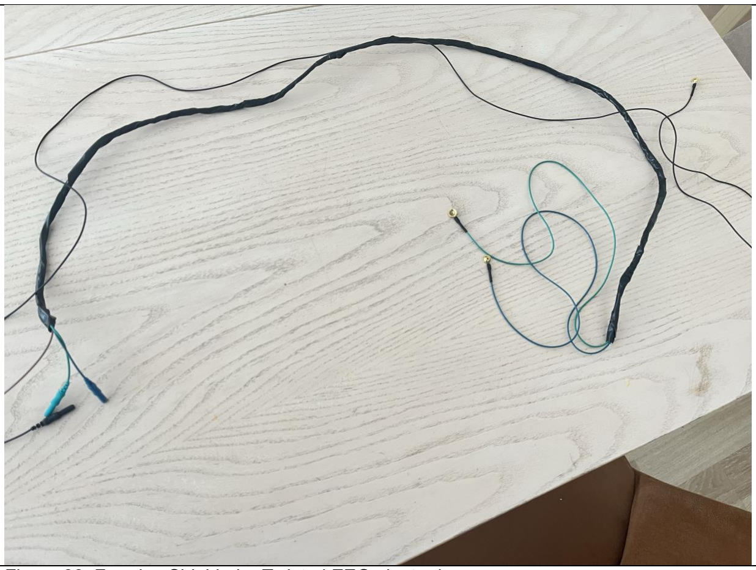
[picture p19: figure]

Figure 22. Faraday Shielded + Twisted EEG electrodes

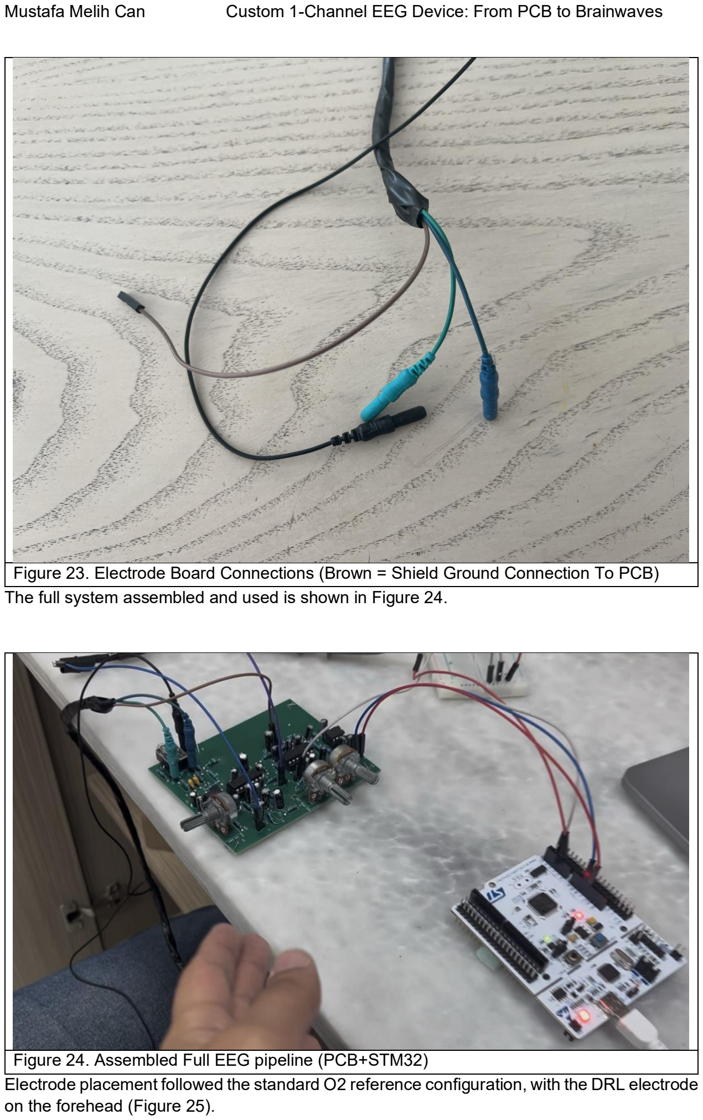
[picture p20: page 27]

Figure 23. Electrode Board Connections (Brown = Shield Ground Connection To PCB) The full system assembled and used is shown in Figure 24.

Figure 24. Assembled Full EEG pipeline (PCB+STM32)
Electrode placement followed the standard O2 reference configuration, with the DRL electrode on the forehead (Figure 25).

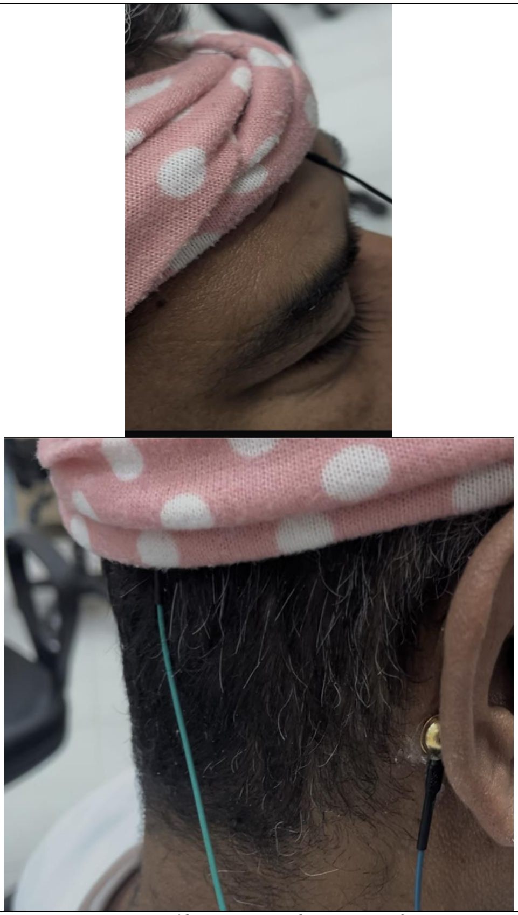
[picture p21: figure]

Figure 25. The electrodes placed (Green = Active O2, Blue = Ref Mastoid Bone, Black = DRL/GND Fz/Forehead)

To also see the real time EEG performance the oscilloscope is connected displaying both outputs of Analog and Digital side on Figure 26. The blue line on the oscilloscpe is the output

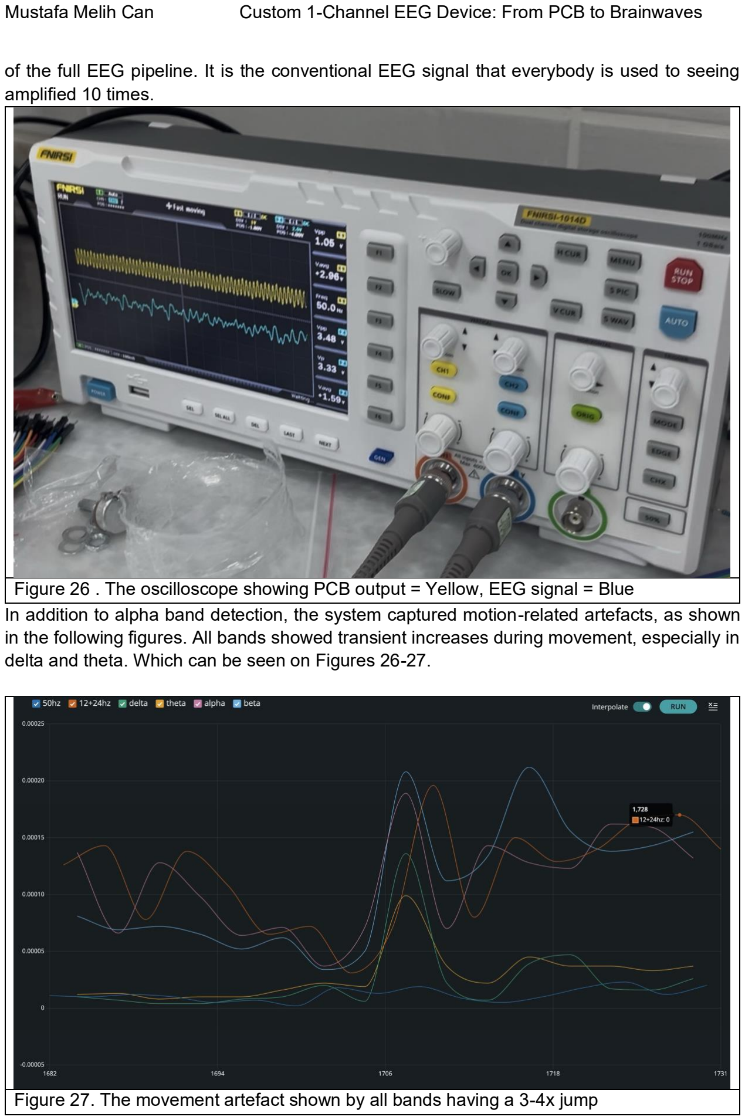
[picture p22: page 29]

of the full EEG pipeline. It is the conventional EEG signal that everybody is used to seeing amplified 10 times.

Figure 26 . The oscilloscope showing PCB output = Yellow, EEG signal = Blue
In addition to alpha band detection, the system captured motion-related artefacts, as shown in the following figures. All bands showed transient increases during movement, especially in delta and theta. Which can be seen on Figures 26-27.

Figure 27. The movement artefact shown by all bands having a 3-4x jump

Figure 28. Jump in delta and theta bands due to movement artefacts

Lets calculate the SNR ratio for the whole system. The values are gotten from the Figure 20.: Psignal = 0.8mWatt
Psignal = 0.2mWatt

SNR = 10 log (

Psignal

Pnoise

) = 10 log(4) = 6.02dB ≈ 6dB

The SNR of 14dB is really good for a DIY system like ours which is in the

Lets calculate the Alpha jump ratio using the observed results in the youtube video which are:
Peyes closed = 0.45mWatt , Peyes open = 0.08mV

Alpℎa Ratio =

Peyes closed

Peyes open

=

0.45
0.08 = 5.6 times jump

As we can see from our calculations that the EEG system is successful in measuring real EEG data from the brain. Typical commercial non-invasive EEG devices have SNR ratio of 5 to 14 dB which for a single channel custom EEG project 6dB SNR ratio therefore shows a successfully built EEG.

# Problems Faced and Solutions

There were multiple problems faced during the creation of this project the table will highlight those problems that you might face as well and their solutions:
THE PROBLEM | THE SOLUTION

The output showed 50Hz signals which you can see the resulting the graph on figure 29. | Added a Digital notch + Increased the gain of DRL circuit + increased the Q of the analog notch filter using the Potentiometer
The SNR was still high after these connections which resulted in the Figure 30. | Shielded the electrodes and grounded the the output which can be seen on figures 22-23 + started using ECG electrodes and swtiched to EEG electrodes which significantly improved SNR
White noise floor was too high resulting in no alpha jumps being observed | Implemented The welch’s method which is a probabilstic algorithm reducing the time uncorralated noise which is white noise in our case.
Electrode connections had high impedance which also causing our electrodes to act as antennas and pick up more 50Hz noise hum | Used EEG electrodes instead of ECG electrodes + used EEG conductive gel
Electrode placement was not 100% accurate causing the signals to be not strong enough | Got a measuring tape and used the 10-20 EEG electrode placement system convention used in hospitals which you can see on Figure 30.

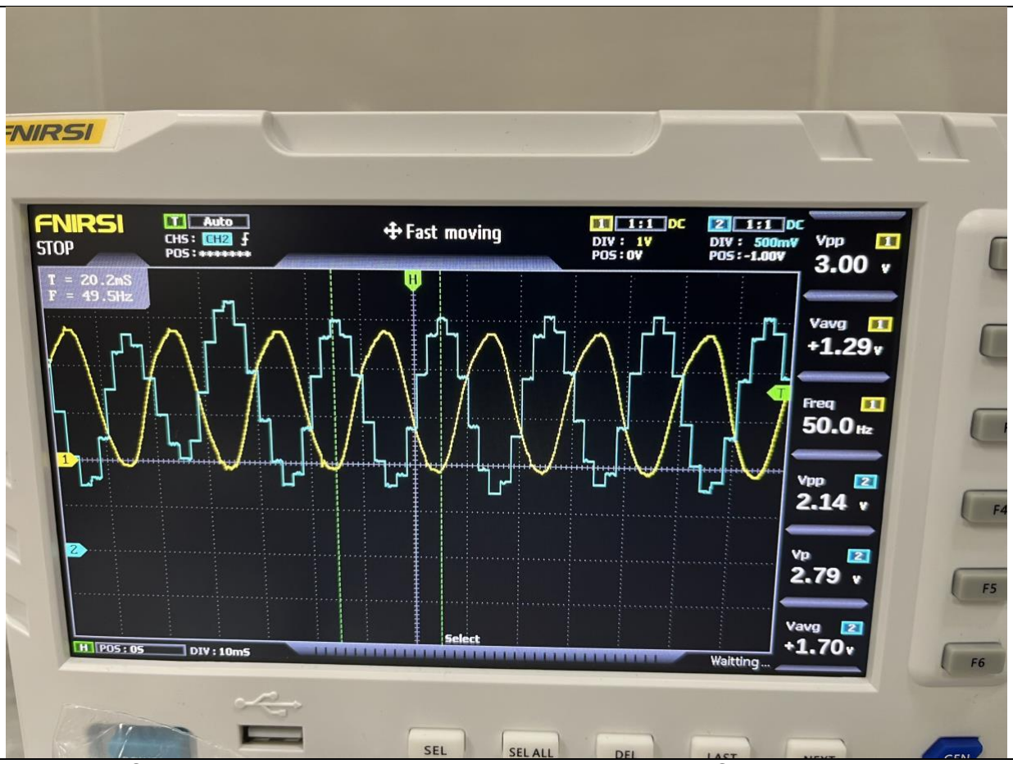
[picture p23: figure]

Figure 29. Output only showing 50Hz correlated signal showing SNR is not high enough.

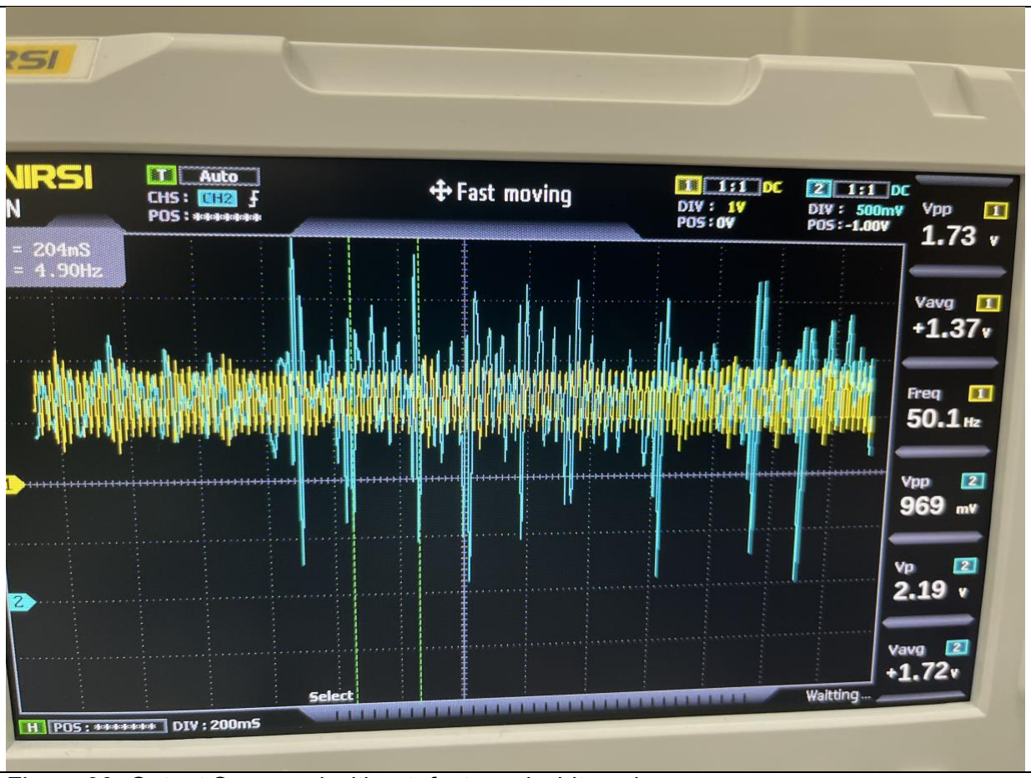
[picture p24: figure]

Figure 30. Output Swamped with artefacts and white noise.

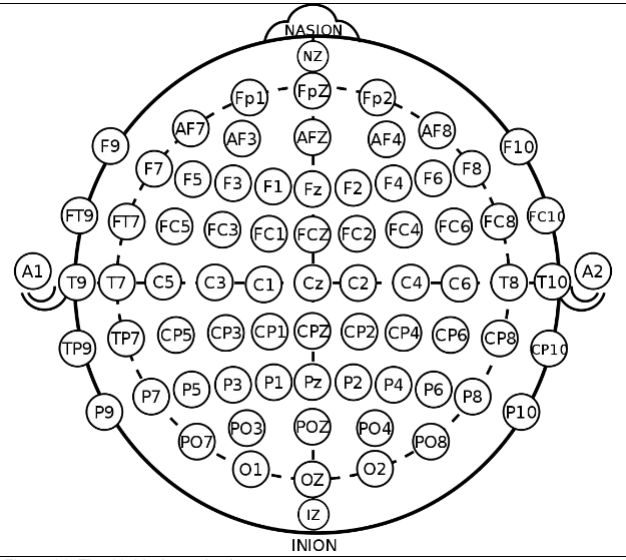
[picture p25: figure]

Figure 31. The 10-20 electrode placement map
After the changes made the signal quality improved and started look more like EEG which you can see the outputs shown in the Results section.

# Conclusion

This project successfully demonstrated the design and implementation of a custom single-channel EEG device, developed from PCB fabrication to real-time brainwave visualization. By combining analog front-end circuitry for amplification and filtering with digital signal processing on an STM32 microcontroller, the system was able to reliably capture and display EEG activity. The device achieved a signal-to-noise ratio in the 6 to 6.8 dB range and achieved a 5.2 Alpha Ratio when the subjects eyes were closed validating its ability to detect genuine neural activity. Key challenges such as 50 Hz interference, electrode impedance, and motion artefacts were addressed through shielding, driven-right-leg circuitry, digital notch filtering, and the application of Welch’s method. While limited by its single-channel architecture and sensitivity to electrode placement, the project establishes a solid foundation for future improvements, including multi-channel expansion, wireless data transfer, and advanced artefact rejection techniques such as ICA/PCA using multiple channels to capture EEG data. Overall this project demonstrates that a low-cost DIY EEG can reach a resonable

SNR levels showing that further EEGs can be made escpecially using DSP methods for research purposes more cheaply and reliably.

# Appendix

Appendix A1. Notch filter derivation part 1

Appendix A2. Notch filter derivation part 2

Appendix A3. Notch filter derivation part 3

Appendix A4. Notch filter derivation part 4

Appendix A5. Notch filter derivation alternative path

Appendix B1. LPF derivation

Appendix B2. LPF derivation

Appendix C1. HPF Derivation

Appendix C2. HPF Derivation

Appendix C3. HPF Derivation

Appendix C4. HPF derivation

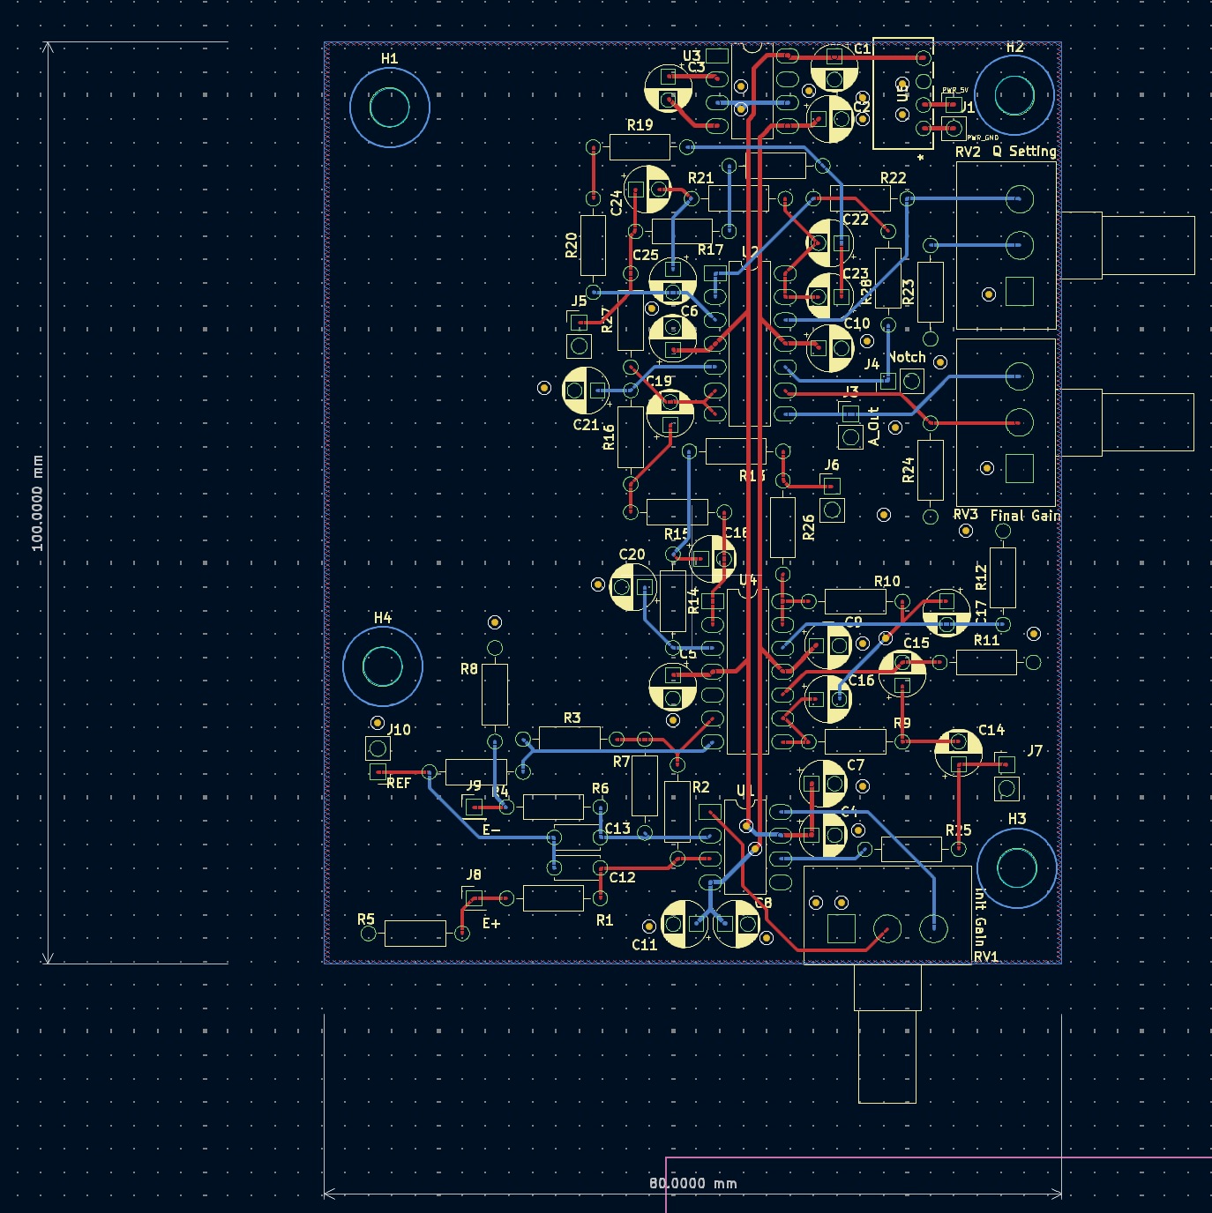
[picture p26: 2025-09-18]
hardware/PCB LAYOUT.jpg

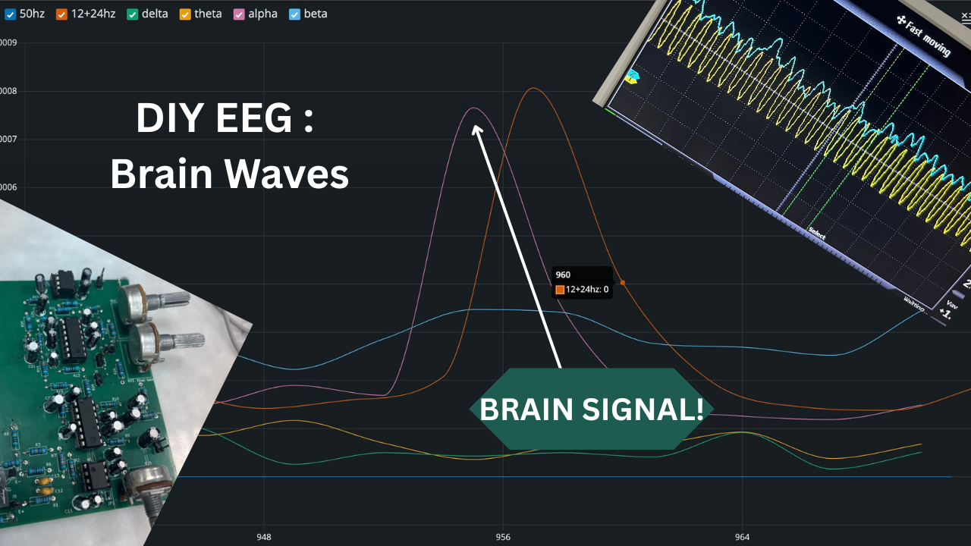
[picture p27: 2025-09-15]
docs/_Project_Thumbnail.png

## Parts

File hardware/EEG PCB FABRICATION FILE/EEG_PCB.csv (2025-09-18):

Id | Designator | Footprint | Quantity | Designation | Supplier and ref
1 | U5 | B0505S-1WR2_MNS | 1 | B0505S-1WR2
2 | C2,C1,C18,C7,C11,C3,C19 | CP_Radial_D5.0mm_P2.50mm | 7 | 10uF
3 | R6,R1 | R_Axial_DIN0207_L6.3mm_D2.5mm_P10.16mm_Horizontal | 2 | 2k2
4 | C6,C5,C9,C8,C4,C10 | CP_Radial_D5.0mm_P2.50mm | 6 | 0.1uF
5 | R21 | R_Axial_DIN0207_L6.3mm_D2.5mm_P10.16mm_Horizontal | 1 | 680
6 | C14,C16,C15,C20,C21,C17 | CP_Radial_D5.0mm_P2.50mm | 6 | 1uF
7 | U2,U4 | DIP-14_W7.62mm_LongPads | 2 | TL074
8 | R16,R14 | R_Axial_DIN0207_L6.3mm_D2.5mm_P10.16mm_Horizontal | 2 | 330
9 | RV1 | Potentiometer_Alps_RK163_Single_Horizontal | 1 | 5k
10 | R13,R15 | R_Axial_DIN0207_L6.3mm_D2.5mm_P10.16mm_Horizontal | 2 | 5k1
11 | R8,R5 | R_Axial_DIN0207_L6.3mm_D2.5mm_P10.16mm_Horizontal | 2 | 1Meg
12 | R12,R11 | R_Axial_DIN0207_L6.3mm_D2.5mm_P10.16mm_Horizontal | 2 | 220k
13 | R28,R26,R27,R25 | R_Axial_DIN0207_L6.3mm_D2.5mm_P10.16mm_Horizontal | 4 | 10
14 | R18,R20 | R_Axial_DIN0207_L6.3mm_D2.5mm_P10.16mm_Horizontal | 2 | 470
15 | J9 | PinHeader_1x01_P2.54mm_Vertical | 1 | E-
16 | J1 | PinHeader_1x02_P2.54mm_Vertical | 1 | Power
17 | RV3 | Potentiometer_Alps_RK163_Single_Horizontal | 1 | 50k
18 | R10,R9 | R_Axial_DIN0207_L6.3mm_D2.5mm_P10.16mm_Horizontal | 2 | 100k
19 | J6 | PinHeader_1x02_P2.54mm_Vertical | 1 | HPF_Out
20 | J4 | PinHeader_1x02_P2.54mm_Vertical | 1 | Notch_Out
21 | R2,R7 | R_Axial_DIN0207_L6.3mm_D2.5mm_P10.16mm_Horizontal | 2 | 47k
22 | J8 | PinHeader_1x01_P2.54mm_Vertical | 1 | E+
23 | C22,C24,C25,C23 | CP_Radial_D5.0mm_P2.50mm | 4 | 2.2uF
24 | J7 | PinHeader_1x02_P2.54mm_Vertical | 1 | Raw_EEG
25 | U3 | DIP-8_W7.62mm_LongPads | 1 | ICL7660
26 | R17,R19 | R_Axial_DIN0207_L6.3mm_D2.5mm_P10.16mm_Horizontal | 2 | 1k
27 | R23 | R_Axial_DIN0207_L6.3mm_D2.5mm_P10.16mm_Horizontal | 1 | 300k
28 | U1 | DIP-8_W7.62mm_LongPads | 1 | AD620
29 | C13,C12 | C_Disc_D4.7mm_W2.5mm_P5.00mm | 2 | 1nF
30 | R22 | R_Axial_DIN0207_L6.3mm_D2.5mm_P10.16mm_Horizontal | 1 | 20k
31 | J5 | PinHeader_1x02_P2.54mm_Vertical | 1 | LPF_Out
32 | R4 | R_Axial_DIN0207_L6.3mm_D2.5mm_P10.16mm_Horizontal | 1 | 470k
33 | J3 | PinHeader_1x02_P2.54mm_Vertical | 1 | Output
34 | R3 | R_Axial_DIN0207_L6.3mm_D2.5mm_P10.16mm_Horizontal | 1 | 680k
35 | J10 | PinHeader_1x02_P2.54mm_Vertical | 1 | Conn_01x02_Pin
36 | RV2 | Potentiometer_Alps_RK163_Single_Horizontal | 1 | 500k
37 | R24 | R_Axial_DIN0207_L6.3mm_D2.5mm_P10.16mm_Horizontal | 1 | 200

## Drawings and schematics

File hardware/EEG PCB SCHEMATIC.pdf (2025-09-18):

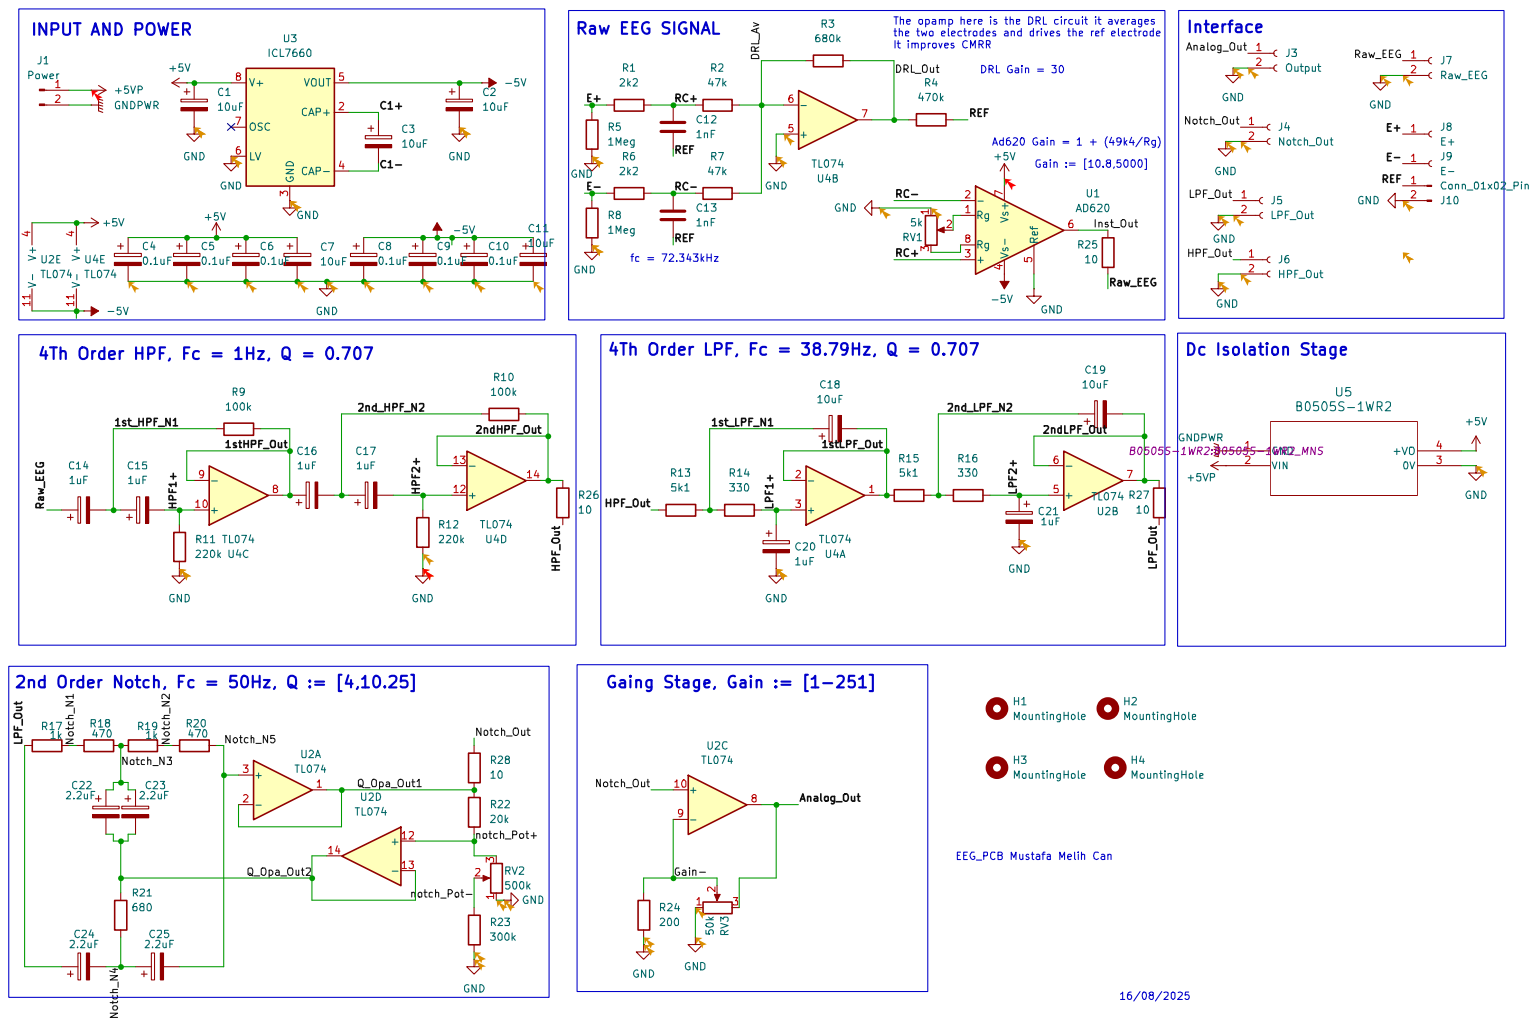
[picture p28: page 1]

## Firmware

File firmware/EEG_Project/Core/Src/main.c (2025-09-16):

/* USER CODE BEGIN Header */
/**
  ******************************************************************************
  * @file           : main.c
  * @brief          : Main program body
  ******************************************************************************
  * @attention
  *
  * Copyright (c) 2025 STMicroelectronics.
  * All rights reserved.
  *
  * This software is licensed under terms that can be found in the LICENSE file
  * in the root directory of this software component.
  * If no LICENSE file comes with this software, it is provided AS-IS.
  *
  ******************************************************************************
  */
/* USER CODE END Header */
/* Includes ------------------------------------------------------------------*/
#include "main.h"

/* Private includes ----------------------------------------------------------*/
/* USER CODE BEGIN Includes */
#include "arm_math.h"
#include <math.h>
#include <string.h>
/* USER CODE END Includes */

/* Private typedef -----------------------------------------------------------*/
/* USER CODE BEGIN PTD */
#define NUM_STAGES   3          // you said: 2 for bandpass + 1 notch
#define BLOCK_SIZE   512        // number of samples you process per call (can be half DMA buffer)
#define FS_HZ       500
//#define FFT_LEN     512
//#define FFT_BINS    (FFT_LEN/2)

////// old code end here
#define SEG_LEN    256
#define HOP        128          // 50% overlap
#define NFFT       SEG_LEN       // main bin length
#define K_TARGET   7			// # of subbins in 2 seconds
#define FFT_BINS   (NFFT/2)     // FFT bins
#define DF_HZ      ((float)FS_HZ/(float)SEG_LEN)
/* USER CODE END PTD */

/* Private define ------------------------------------------------------------*/
/* USER CODE BEGIN PD */

/* USER CODE END PD */

/* Private macro -------------------------------------------------------------*/
/* USER CODE BEGIN PM */

/* USER CODE END PM */

/* Private variables ---------------------------------------------------------*/
ADC_HandleTypeDef hadc3;
DMA_HandleTypeDef hdma_adc3;

DAC_HandleTypeDef hdac;
DMA_HandleTypeDef hdma_dac1;

TIM_HandleTypeDef htim8;

UART_HandleTypeDef huart2;

/* USER CODE BEGIN PV */
volatile uint32_t Buffer_Length = 512;
uint16_t adc_buf[512];   // DMA buffer for ADC samples
uint16_t work_buf1[512];
uint16_t work_buf2[512];// a buffer for me to use to do math dc removal/windowing/filtering etc.
uint16_t out_buf[512];
volatile uint8_t which_half = 0;
volatile uint8_t buffer_ready = 0;
static float dac_scale = 15.0f;   //
/////////////////////////////////////////////////////////////////////////// Filter coefficients
float biquad_coeffs[NUM_STAGES * 5] = {
    0.0366f, 0.0731f, 0.0366f, 1.3909f, -0.5372f,   // LPF coefiicients b0, b1, b2, a1, a2 BE CAREFUL THIS PROGRAM FLIPS THE SIGNS OF A COEFFICIENTS
	1.0000f,-1.6180f, 1.0000f, 1.6019f, -0.9801f,  //Notch coefiieicnts b0, b1, b2, a1, a2
	1.0000f,-2.0000f, 1.0000f, 1.9800f, -0.9801f,  //HPF coefiieicnts b0, b1, b2, a1, a2
};
/////////////////////////////////////////////////////////////////////////// Filter coefficients
/////////////////////////////////////////////////////////////////////////// Filtering Variables
float biquad_state[NUM_STAGES * 2];
arm_biquad_cascade_df2T_instance_f32 biquadS;

static float in_f[BLOCK_SIZE];
static float out_f[BLOCK_SIZE];
/////////////////////////////////////////////////////////////////////////// Filtering Variables

///////////////////////////////////////////////////////////////////////////	FFT variables
//arm_rfft_fast_instance_f32 rfft;
//static float fft_in[FFT_LEN];
//static float fft_out[FFT_LEN];
//float mag[(FFT_LEN/2)+1];
//float hann[FFT_LEN];
//static uint16_t k_max = 55;
float EEG_DATA[6]; // indices: 0 = delta; 1 = theta; 2 = alpha; 3 = beta; 4 = 50hz hum; 5 = power band of 12HZ+24Hz
///// old code end here

// Welch / Hamming state
static float ring[SEG_LEN*2];          // copy-free overlap
static int   wr = 0, newCount = 0, K = 0;

arm_rfft_fast_instance_f32 rfft;
static float ham[SEG_LEN];             // Hamming window
static float U = 0.0f;                 // window power (≈0.3974 for Hamming 256)
static float seg[SEG_LEN];
static float fft_in[NFFT], fft_out[NFFT];

static float psd_accum[NFFT/2 + 1]; // psd means power spectral density = power of frequency spectrum basically
static float psd[NFFT/2 + 1];



///////////////////////////////////////////////////////////////////////////	FFT variables


/* USER CODE END PV */

/* Private function prototypes -----------------------------------------------*/
void SystemClock_Config(void);
static void MX_GPIO_Init(void);
static void MX_DMA_Init(void);
static void MX_ADC3_Init(void);
static void MX_USART2_UART_Init(void);
static void MX_DAC_Init(void);
static void MX_TIM8_Init(void);
/* USER CODE BEGIN PFP */
static void print_stats(uint16_t *p, size_t n);
static void DMA_Tester(void);
static void Dc_Removal(const uint16_t *in, uint16_t *out, size_t n);
static void ADC_DAC_test (uint16_t *in, uint16_t *out, size_t n);
static void process_block(uint16_t *in, uint16_t *out, size_t n);
static void my_fft_block (const uint16_t *in, float *hann, uint16_t k_max);  // FFT pipeline
static void init_hamming(void);
static void Bandpower(const float *in);
static void EEG_OUT(void);
static void init_hann_window(void); // comment from here to go back to previous version
static void Bandpower_from_psd(const float *Sxx, float df);
static void welch_process_segment(void);
static inline void welch_push_sample(float x);
static void EEG_OUT2(void);
/* USER CODE END PFP */

/* Private user code ---------------------------------------------------------*/
/* USER CODE BEGIN 0 */
#include <stdio.h>
int __io_putchar(int ch) {
  extern UART_HandleTypeDef huart2;
  HAL_UART_Transmit(&huart2, (uint8_t*)&ch, 1, 10);
  return ch;
}
/* USER CODE END 0 */

/**
  * @brief  The application entry point.
  * @retval int
  */
int main(void)
{

  /* USER CODE BEGIN 1 */

  /* USER CODE END 1 */

  /* MCU Configuration--------------------------------------------------------*/

  /* Reset of all peripherals, Initializes the Flash interface and the Systick. */
  HAL_Init();

  /* USER CODE BEGIN Init */

  /* USER CODE END Init */

  /* Configure the system clock */
  SystemClock_Config();

  /* USER CODE BEGIN SysInit */

  /* USER CODE END SysInit */

  /* Initialize all configured peripherals */
  MX_GPIO_Init();
  MX_DMA_Init();
  MX_ADC3_Init();
  MX_USART2_UART_Init();
  MX_DAC_Init();
  MX_TIM8_Init();
  /* USER CODE BEGIN 2 */
  HAL_ADC_Start_DMA(&hadc3, (uint32_t*)adc_buf, Buffer_Length);
  HAL_DAC_Start(&hdac, DAC_CHANNEL_1);
  HAL_TIM_Base_Start(&htim8);
  arm_biquad_cascade_df2T_init_f32(&biquadS, NUM_STAGES,biquad_coeffs,biquad_state);
  arm_rfft_fast_init_f32(&rfft, NFFT);   // Init FFT
  init_hamming();
  memset(psd_accum, 0, sizeof(psd_accum));
  K = 0;
//  init_hann_window();                       // Fill hann[] table /////// to go back to previous version uncomment
  printf("delta,theta,alpha,beta\n");
  /* USER CODE END 2 */

  /* Infinite loop */
  /* USER CODE BEGIN WHILE */
  while (1)
  {
	  if (buffer_ready){
		  Dc_Removal(adc_buf, work_buf1, Buffer_Length); // the processing that we do
		  process_block(work_buf1, out_buf,Buffer_Length);

//		  ADC_DAC_test(adc_buf, out_buf, Buffer_Length);
		  HAL_DAC_Stop_DMA(&hdac, DAC_CHANNEL_1);
		  HAL_DAC_Start_DMA(&hdac, DAC_CHANNEL_1, (uint32_t*)out_buf, Buffer_Length, DAC_ALIGN_12B_R);
//		  //// uncomment for the previus fft block
//		  my_fft_block(out_buf,hann,k_max); //FFT function
//		  Bandpower(mag);
//		  EEG_OUT();

		  for (size_t i=0; i<Buffer_Length; i++){
		      welch_push_sample(out_f[i]);   // analyze filtered float stream
		  }



		  buffer_ready  = 0;
	  }




//	  DMA_Tester();
//	  HAL_Delay(20);
//	  HAL_GPIO_TogglePin(LED2_GPIO_Port,LED2_Pin);

//	  printf("Hello UART2!\r\n");
//	  HAL_Delay(1000);
    /* USER CODE END WHILE */

    /* USER CODE BEGIN 3 */
  }
  /* USER CODE END 3 */
}

/**
  * @brief System Clock Configuration
  * @retval None
  */
void SystemClock_Config(void)
{
  RCC_OscInitTypeDef RCC_OscInitStruct = {0};
  RCC_ClkInitTypeDef RCC_ClkInitStruct = {0};

  /** Configure the main internal regulator output voltage
  */
  __HAL_RCC_PWR_CLK_ENABLE();
  __HAL_PWR_VOLTAGESCALING_CONFIG(PWR_REGULATOR_VOLTAGE_SCALE3);

  /** Initializes the RCC Oscillators according to the specified parameters
  * in the RCC_OscInitTypeDef structure.
  */
  RCC_OscInitStruct.OscillatorType = RCC_OSCILLATORTYPE_HSI;
  RCC_OscInitStruct.HSIState = RCC_HSI_ON;
  RCC_OscInitStruct.HSICalibrationValue = RCC_HSICALIBRATION_DEFAULT;
  RCC_OscInitStruct.PLL.PLLState = RCC_PLL_NONE;
  if (HAL_RCC_OscConfig(&RCC_OscInitStruct) != HAL_OK)
  {
    Error_Handler();
  }

  /** Initializes the CPU, AHB and APB buses clocks
  */
  RCC_ClkInitStruct.ClockType = RCC_CLOCKTYPE_HCLK|RCC_CLOCKTYPE_SYSCLK
                              |RCC_CLOCKTYPE_PCLK1|RCC_CLOCKTYPE_PCLK2;
  RCC_ClkInitStruct.SYSCLKSource = RCC_SYSCLKSOURCE_HSI;
  RCC_ClkInitStruct.AHBCLKDivider = RCC_SYSCLK_DIV1;
  RCC_ClkInitStruct.APB1CLKDivider = RCC_HCLK_DIV1;
  RCC_ClkInitStruct.APB2CLKDivider = RCC_HCLK_DIV1;

  if (HAL_RCC_ClockConfig(&RCC_ClkInitStruct, FLASH_LATENCY_0) != HAL_OK)
  {
    Error_Handler();
  }
}

/**
  * @brief ADC3 Initialization Function
  * @param None
  * @retval None
  */
static void MX_ADC3_Init(void)
{

  /* USER CODE BEGIN ADC3_Init 0 */

  /* USER CODE END ADC3_Init 0 */

  ADC_ChannelConfTypeDef sConfig = {0};

  /* USER CODE BEGIN ADC3_Init 1 */

  /* USER CODE END ADC3_Init 1 */

  /** Configure the global features of the ADC (Clock, Resolution, Data Alignment and number of conversion)
  */
  hadc3.Instance = ADC3;
  hadc3.Init.ClockPrescaler = ADC_CLOCK_SYNC_PCLK_DIV4;
  hadc3.Init.Resolution = ADC_RESOLUTION_12B;
  hadc3.Init.ScanConvMode = DISABLE;
  hadc3.Init.ContinuousConvMode = DISABLE;
  hadc3.Init.DiscontinuousConvMode = DISABLE;
  hadc3.Init.ExternalTrigConvEdge = ADC_EXTERNALTRIGCONVEDGE_RISING;
  hadc3.Init.ExternalTrigConv = ADC_EXTERNALTRIGCONV_T8_TRGO;
  hadc3.Init.DataAlign = ADC_DATAALIGN_RIGHT;
  hadc3.Init.NbrOfConversion = 1;
  hadc3.Init.DMAContinuousRequests = ENABLE;
  hadc3.Init.EOCSelection = ADC_EOC_SINGLE_CONV;
  if (HAL_ADC_Init(&hadc3) != HAL_OK)
  {
    Error_Handler();
  }

  /** Configure for the selected ADC regular channel its corresponding rank in the sequencer and its sample time.
  */
  sConfig.Channel = ADC_CHANNEL_13;
  sConfig.Rank = 1;
  sConfig.SamplingTime = ADC_SAMPLETIME_480CYCLES;
  if (HAL_ADC_ConfigChannel(&hadc3, &sConfig) != HAL_OK)
  {
    Error_Handler();
  }
  /* USER CODE BEGIN ADC3_Init 2 */

  /* USER CODE END ADC3_Init 2 */

}

/**
  * @brief DAC Initialization Function
  * @param None
  * @retval None
  */
static void MX_DAC_Init(void)
{

  /* USER CODE BEGIN DAC_Init 0 */

  /* USER CODE END DAC_Init 0 */

  DAC_ChannelConfTypeDef sConfig = {0};

  /* USER CODE BEGIN DAC_Init 1 */

  /* USER CODE END DAC_Init 1 */

  /** DAC Initialization
  */
  hdac.Instance = DAC;
  if (HAL_DAC_Init(&hdac) != HAL_OK)
  {
    Error_Handler();
  }

  /** DAC channel OUT1 config
  */
  sConfig.DAC_Trigger = DAC_TRIGGER_T8_TRGO;
  sConfig.DAC_OutputBuffer = DAC_OUTPUTBUFFER_ENABLE;
  if (HAL_DAC_ConfigChannel(&hdac, &sConfig, DAC_CHANNEL_1) != HAL_OK)
  {
    Error_Handler();
  }
  /* USER CODE BEGIN DAC_Init 2 */

  /* USER CODE END DAC_Init 2 */

}
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

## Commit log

2025-09-15 Rename Custom 1-Channel EEG Device From PCB to Brainwaves.pdf to docs/Custom 1-Channel EEG Device From PCB to Brainwaves.pdf
2025-09-15 Update and rename docs/Custom 1-Channel EEG Device From PCB to Brainwaves.pdf to Custom 1-Channel EEG Device From PCB to Brainwaves.pdf
2025-09-15 Update Custom 1-Channel EEG Device From PCB to Brainwaves.pdf
2025-09-15 Update and rename Custom 1-Channel EEG Device From PCB to Brainwaves.pdf to docs/Custom 1-Channel EEG Device From PCB to Brainwaves.pdf
2025-09-15 Rename EEG Circuit Simulation .asc to docs/EEG Circuit Simulation .asc
2025-09-15 Rename PCB LAYOUT.jpg to docs/PCB LAYOUT.jpg
2025-09-15 Rename EEG PCB FABRICATION FILE.zip to hardware/EEG PCB FABRICATION FILE.zip
2025-09-15 Rename Custom 1-Channel EEG Device From PCB to Brainwaves.pdf to _Custom_1-Channel_EEG_Device_From_PCB_to_Brainwaves.pdf
2025-09-16 Rename PCB LAYOUT.jpg to PCB LAYOUT.jpg
2025-09-16 Rename EEG Circuit Simulation .asc to EEG Circuit Simulation .asc
2025-09-16 Unpacked firmware and hardware zips into proper folders
    [EEG_PCB-B_Cu.gbr, EEG_PCB-B_Fab.gbr, EEG_PCB-B_Mask.gbr, EEG_PCB-B_Paste.gbr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]
2025-09-18 Added the KiCAD files + Added Galvanic Decoupling to make the project safer
    [EEG_PCB-B_Cu.gbr, EEG_PCB-B_Fab.gbr, EEG_PCB-B_Mask.gbr, EEG_PCB-B_Paste.gbr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]
2025-09-18 Added Updated Schematic and PCB layout as photos
